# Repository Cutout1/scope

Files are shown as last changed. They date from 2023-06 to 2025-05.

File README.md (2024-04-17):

# Scopocket: A Low-Cost Oscilloscope for Education
Welcome to the GitHub repository for the Scopocket project. Here you can find the schematics, PCB fabrication files, and source code for the Scopocket. For additional information please visit [the documentation webpage.](https://scopocket.com)

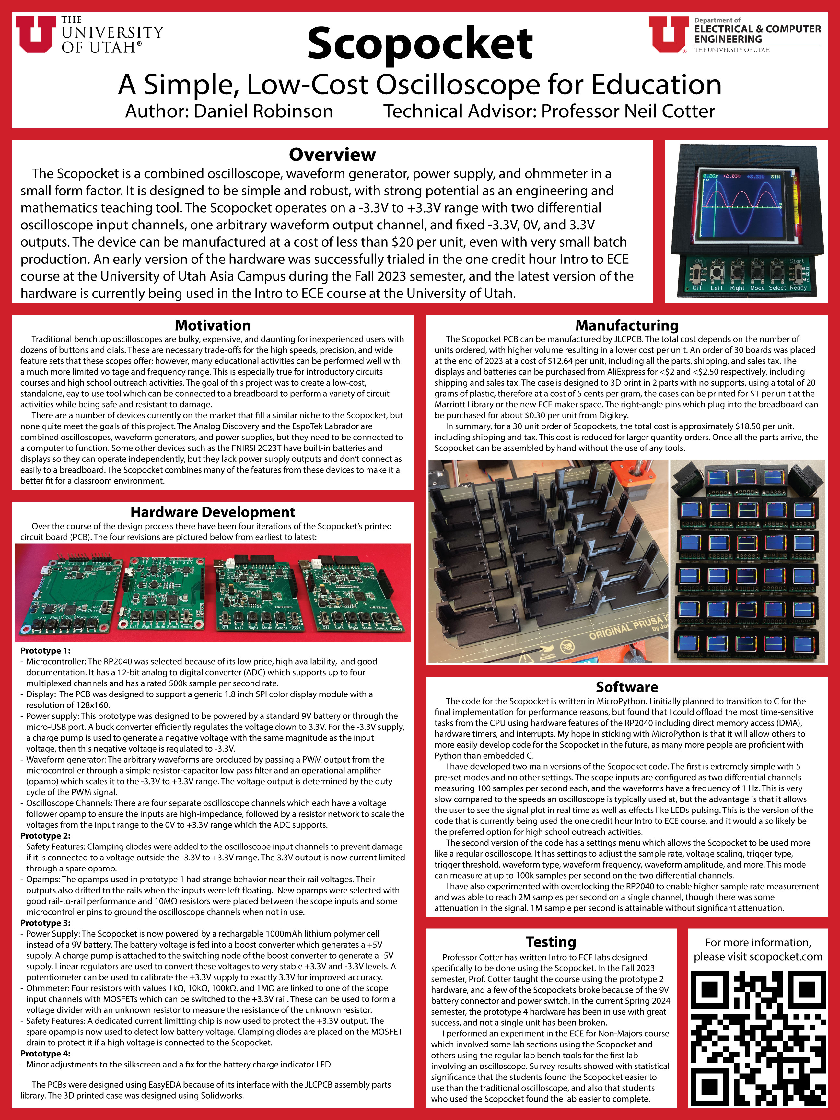
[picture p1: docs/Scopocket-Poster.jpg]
Scopocket Poster


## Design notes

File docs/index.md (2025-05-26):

---
layout: default
title: Scopocket
auto_title: false
---

# Overview

The Scopocket is a combined oscilloscope, function generator, ohmmeter, power supply, and more in a simple and compact package. It is primarily designed to be an educational tool with its main strengths being ease of use and low cost (being manufacturable for less than $20 per unit), with the tradeoff of having a quite limited voltage and frequency range.

The schematics, PCB fabrication files, source code, and case 3D models can all be found in [the GitHub repository.](https://github.com/Cutout1/scope)

A collection of lab activities designed to teach math concepts using the Scopocket can be found [on this Canvas site.](https://utah.instructure.com/courses/1191496)

The navigation bar on the left contains links to a number of informational pages.

Scopocket

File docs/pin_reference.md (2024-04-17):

---
id: pin-reference
title: Pin Reference
---

This page gives a detailed breakdown of what each pin on the Scopocket does. There are also pin labels on the underside of the Scopocket.

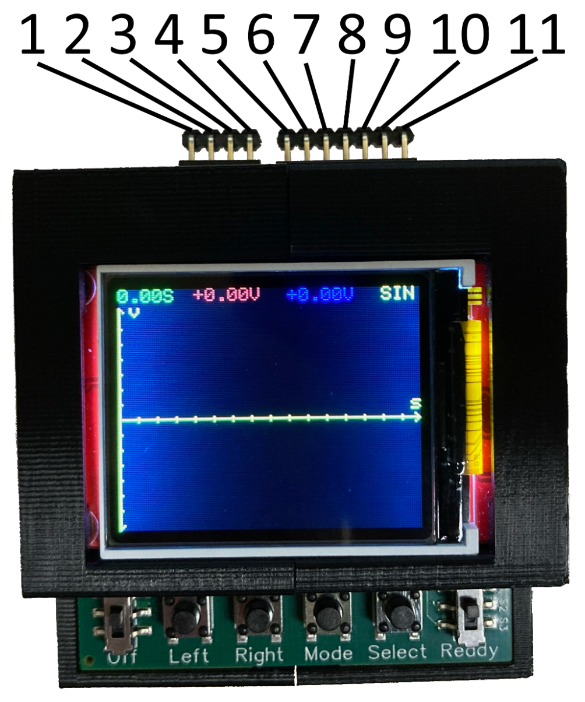
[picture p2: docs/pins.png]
Scopocket Pins


1. **Channel 1 Reference:** Reference voltage input for the oscilloscope’s first channel, which is plotted in red.
2. **Channel 1:** Voltage input for the oscilloscope’s first channel. The value that is plotted is equal to the voltage at this pin subtracted by the voltage at pin 1.
3. **Channel 2 Reference:** Reference voltage input for the oscilloscope’s first channel, which is plotted in blue.
4. **Channel 2:** Voltage input for the oscilloscope’s first channel. The value that is plotted is equal to the voltage at this pin subtracted by the voltage at pin 3.
5. **3.3V Output:** This pin outputs a steady 3.3V, limited to 75mA.
6. **0V Reference:** This pin outputs 0V.
7. **-3.3V Output:** This pin outputs a steady negative 3.3V, limited to 250mA.
8. **Switch 1:** This pin is connected to pin 9 when the switch is in the “Start” position.
9. **Switch 2:** This pin is connected to pin 8 when the switch is in the “Start” position, and it is connected to pin 10 when the switch is in the “Ready” position.
10. **Switch 3:** This pin is connected to pin 9 when the switch is in the “Ready” position.
11. **Waveform Output:** A configurable waveform is output with an amplitude up to 3.3V.

## Buttons and Switches
**Power Switch:** The switch on the left turns the Scopocket on and off. To preserve battery life, turn the Scopocket off when not in use.

**Left Button:** The left button is used to move the cursor left when reading a measured waveform. It may also be used to navigate the settings menu.

**Right Button:** The right button is used to move the cursor right when reading a measured waveform. It may also be used to navigate the settings menu.

**Mode Button:** The mode button is used to change the current settings of the Scopocket.

**Select Button:** The select button is used in the settings menu to select the currently underlined option. (Advanced software only)

**Trigger switch:** A recording can be triggered by moving the switch on the right from the “Ready” position to the “Start” position. It also changes the connection between pins 8, 9 and 10, as described in the previous section.

## Modes (Simple software only)
**SIN:** 2-channel oscilloscope sampling at 100 samples per second with a 1 Hz sine wave output from the waveform generator. Measurement begins immediately when the trigger switch is moved from “Ready” to “Start.”

**SQR:** 2-channel oscilloscope sampling at 100 samples per second with a 1 Hz square wave output from the waveform generator. Measurement begins immediately when the trigger switch is moved from “Ready” to “Start.”

**PHS:** 2-channel oscilloscope sampling at 100 samples per second with a 1 Hz sine wave output from the waveform generator. Measurement begins at the next peak of the output sine wave after the trigger switch is moved from “Ready” to “Start.”

**PWR:** This mode plots the power draw of a component in series with a 1kΩ resistor. To perform the measurement, place the channel 1 probes across a 1kΩ resistor in series with the load, and place the channel 2 probes across the load. Measurement begins when the load current reaches a peak. The power measurement is sampled at 100 samples per second, and a 1 Hz sine wave is output from the waveform generator.

**OHM:** Resistance measurement mode. To perform measurement, connect a resistor or resistor network between the channel 1 input and ground (pin 2 and pin 6). The screen will immediately display the resistance value in ohms.

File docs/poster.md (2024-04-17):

---
id: poster
title: Poster
auto_title: false
---

Scopocket Poster

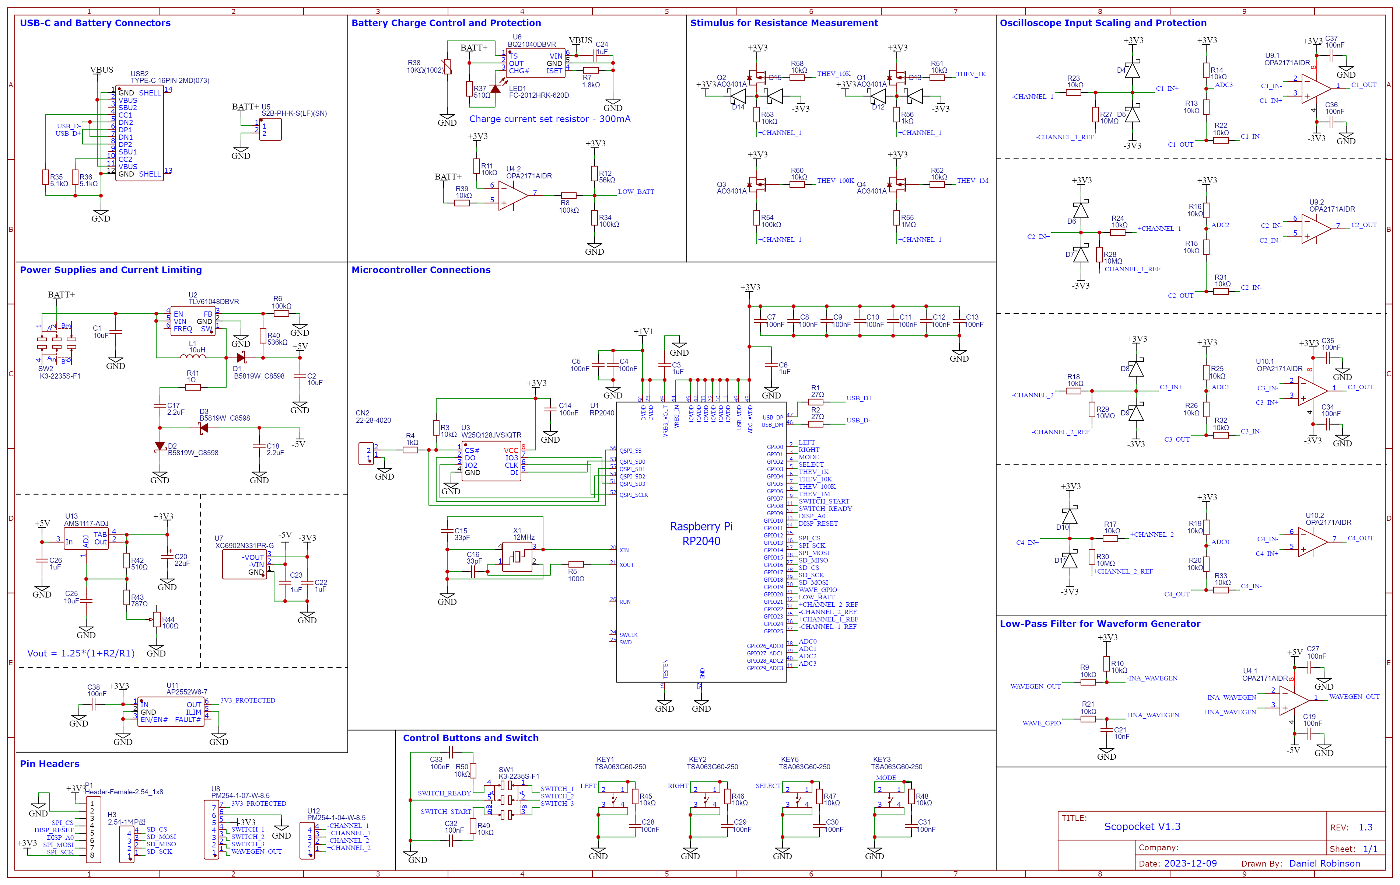
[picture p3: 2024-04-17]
Schematic/Scopocket Schematic V1.3.png

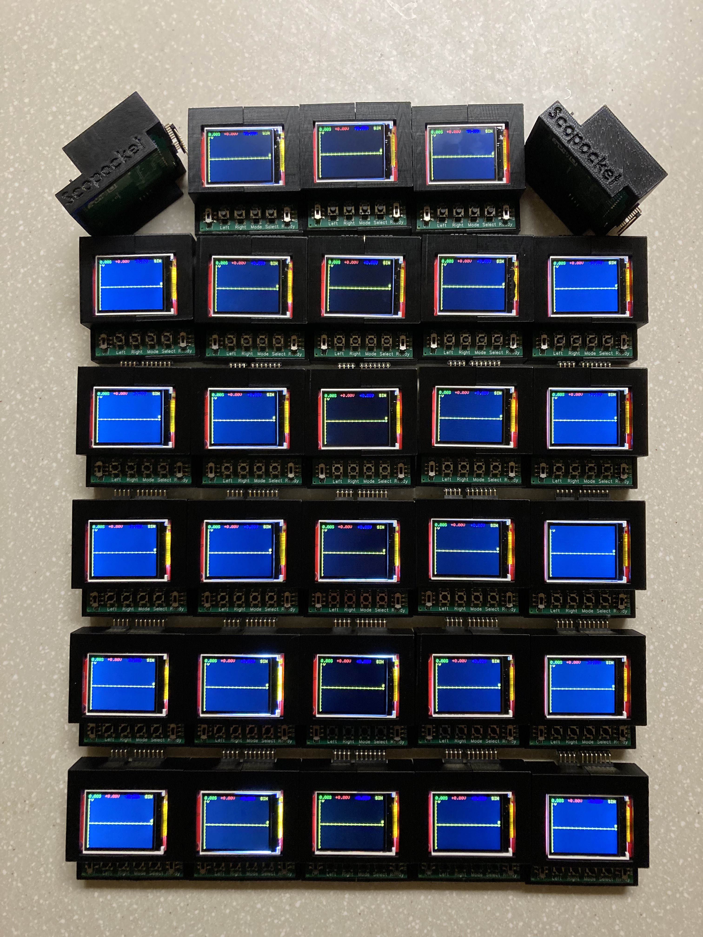
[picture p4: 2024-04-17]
docs/Thirty-Scopockets.jpg

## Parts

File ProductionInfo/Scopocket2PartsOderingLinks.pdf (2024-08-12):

Scopocket 2 Parts Ordering Links as of 2024/06/27

Batteries:
Ali Express
https://www.aliexpress.us/item/2251832658151463.html
10 PCS 3.7V 1000mAh 503450 Lithium Polymer LiPo Rechargeable Battery JST PH 2.0 2pin Plug For Mp3 DVD PAD Camera Recorder

Displays (Be sure to select the 1.8 TFT option) :
Ali Express
https://www.aliexpress.us/item/2255801096152347.html
TFT Display 0.96/1.3/1.44/1.77/1.8/2.0/2.4/2.8 inch IPS 7P SPI HD 65K Full Color LCD Module ST7735 Drive IC 80*160 For Arduino

Headers (40-pin headers may be manually snapped apart to make 3 7-pin headers, 4 4-pin headers) Digi-Key part number: S1132EC-40-ND (https://www.digikey.com/en/products/detail/sullins-connector-solutions/PRPC040SBCN-M71RC/2776146?s=N4IgTCBcDaIMoEYEGYwFEDCBaALABiwDkAREAXQF8g)
Manufacturer part number: PRPC040SB CN-M71RC (Sullins Connector Solutions)
Part Description: Conn Header R/A 40pos 2.54mm
100 @ $0.8275 = $82.75

Fish paper (battery insulator)
145ptags.com
https://www.145ptags.com/product-page/cg100325ftd-fish-paper-roll-3in-x-25ft-dark 145ptags.com
CG100325FTD Fish Paper Roll 3in. x 25' x 0.01" (Dark)

OBS:
Fish paper (battery insulator)
Digi-Key part number 36-117-ND (https://www.digikey.com/en/products/detail/keystone-electronics/117/7385294)
Manufacturer: Keystone Electronics Battery Insulator Pull Tab 1=1PC 500 @ $0.06554 = $32.77

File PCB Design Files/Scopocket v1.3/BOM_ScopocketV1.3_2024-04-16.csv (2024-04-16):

ID | Name | Designator | Footprint | Quantity | Manufacturer Part | Manufacturer | Supplier | Supplier Part | Price | Pins
1 | 100nF | C4,C5,C7,C8,C9,C10,C11,C12,C13,C14,C19,C27,C28,C29,C30,C31,C32,C33,C34,C35,C36,C37,C38 | C0402 | 23 | CL05B104KO5NNNC | SAMSUNG(三星) | LCSC | C1525 | 0.001 | 2
2 | 10KΩ(1002) | R38 | R0603 | 1 | NCP18XH103F03RB | muRata(村田) | LCSC | C13564 | 0.032 | 2
3 | Header-Female-2.54_1x8 | P1 | HDR-TH_8P-P2.54-V-F-1 | 1 | 2.54-1*8P母环保 | BOOMELE(博穆精密) | LCSC | C27438 | 0.07 | 8
4 | K3-2235S-F1 | SW1,SW2 | SW-SMD_K3-2235S-F1 | 2 | K3-2235S-F1 | 韩国韩荣 | LCSC | C223858 | 0.139 | 6
5 | OPA2171AIDR | U9,U4,U10 | SOIC-8_L5.0-W4.0-P1.27-LS6.0-BL | 3 | OPA2171AIDR | TI(德州仪器) | LCSC | C40904 | 0.356 | 8
6 | PM254-1-07-W-8.5 | U8 | HDR-TH_7P-P2.54-H-F-W10.0-N | 1 | PM254-1-07-W-8.5 | HCTL(华灿天禄) | LCSC | C2897389 | 0.147 | 7
7 | PM254-1-04-W-8.5 | U12 | HDR-TH_4P-P2.54-H-F-W10.0-N | 1 | PM254-1-04-W-8.5 | HCTL(华灿天禄) | LCSC | C2897386 | 0.096 | 4
8 | 10uF | C1,C2 | C0603 | 2 | CL10A106MA8NRNC | SAMSUNG(三星) | LCSC | v |  | 2
9 | 10uF | C25 | C0603 | 1 | CL10A106MA8NRNC | SAMSUNG(三星) | LCSC | C96446 | 0.017 | 2
10 | 1uF | C3,C6,C22,C23,C26,C24 | C0402 | 6 | CL05A105KA5NQNC | SAMSUNG | LCSC | C52923 | 0.004 | 2
11 | 33pF | C15,C16 | C0402 | 2 | 0402CG330J500NT | FH | LCSC | C1562 | 0.001 | 2
12 | 10nF | C21 | C0402 | 1 | CL05B103KB5NNNC | SAMSUNG(三星) | LCSC | C15195 | 0.001 | 2
13 | 2.2uF | C17,C18 | C1206 | 2 | CL31B225KBHNNNE | SAMSUNG(三星) | LCSC | C50254 | 0.028 | 2
14 | 22uF | C20 | CASE-A_3216 | 1 | CA45-A-10V-22uF-K | CEC(振华新云) | LCSC | C129272 | 0.064 | 2
15 | B5819W_C8598 | D1,D2,D3 | SOD-123_L2.7-W1.6-LS3.7-RD-1 | 3 | B5819W SL | CJ(江苏长电/长晶) | LCSC | C8598 | 0.025 | 2
16 | BAS100CS-AU_R1_000A1 | D4,D5,D6,D7,D8,D9,D10,D11,D12,D13,D14,D15 | SOD-323 | 12 | BAS100CS-AU_R1_000A1 | PANJIT International | LCSC | C2999088 | 0.056 | 2
17 | 2.54-1*4P母 | H3 | HDR-TH_4P-P2.54-V-F | 1 | 2.54-1*4P母 | BOOMELE(博穆精密) | LCSC | C2718488 | 0.041 | 4
18 | TSA063G60-250 | KEY1,KEY2,KEY3,KEY5 | KEY-SMD_4P-L6.1-W6.1-P4.50-LS9.0 | 4 | TSA063G60-250 | BRIGHT(博瑞泰) | LCSC | C294566 | 0.025 | 4
19 | 10uH | L1 | IND-SMD_L4.0-W4.0 | 1 | SWPA4030S100MT | Sunlord(顺络) | LCSC | C38117 | 0.046 | 2
20 | FC-2012HRK-620D | LED1 | LED0805-R-RD | 1 | NCD0805R1 | 国星光电 | LCSC | C84256 | 0.012 | 2
21 | AO3401A | Q1,Q2,Q3,Q4 | SOT-23_L2.9-W1.3-P1.90-LS2.4-BR | 4 | AO3401A | AOS | LCSC | C15127 | 0.053 | 3
22 | 27Ω | R1,R2 | R0603 | 2 | 0603WAF270JT5E | UniOhm | LCSC | C25190 | 0.001 | 2
23 | 10kΩ | R3,R9,R10,R11,R13,R14,R15,R16,R17,R18,R19,R20,R21,R22,R23,R24,R25,R26,R31,R32,R33,R39,R45,R46,R47,R48,R49,R50,R51,R53,R58,R60,R62 | R0603 | 33 | 0603WAF1002T5E | UniOhm | LCSC | C25804 | 0.001 | 2
24 | 1kΩ | R4,R56 | R0603 | 2 | 0603WAF1001T5E | UniOhm | LCSC | C21190 | 0.001 | 2
25 | 100kΩ | R6,R8,R34,R54 | R0603 | 4 | 0603WAF1003T5E | UNI-ROYAL(厚声) | LCSC | C25803 | 0.001 | 2
26 | 100Ω | R5 | R0402 | 1 | 0402WGF1000TCE | UniOhm | LCSC | C25076 | 0.001 | 2
27 | 1.8kΩ | R7 | R0603 | 1 | 0603WAF1801T5E | UNI-ROYAL(厚声) | LCSC | C4177 | 0.001 | 2
28 | 56kΩ | R12 | R0603 | 1 | 0603WAF5602T5E | UNI-ROYAL(厚声) | LCSC | C23206 | 0.001 | 2
29 | 510Ω | R37,R42 | R0603 | 2 | 0603WAF5100T5E | UNI-ROYAL(厚声) | LCSC | C23193 | 0.001 | 2
30 | 536kΩ | R40 | R0603 | 1 | RS-03K5363FT | FH(风华) | LCSC | C321940 | 0.001 | 2
31 | 787Ω | R43 | R0603 | 1 | 0603WAF7870T5E | UNI-ROYAL(厚声) | LCSC | C23111 | 0.001 | 2
32 | 1MΩ | R55 | R0603 | 1 | 0603WAF1004T5E | UNI-ROYAL(厚声) | LCSC | C22935 | 0.001 | 2
33 | 10MΩ | R27,R28,R29,R30 | R0402 | 4 | RTT02106JTH | RALEC(旺诠) | LCSC | C102764 |  | 2
34 | 5.1kΩ | R35,R36 | R0402 | 2 | RC-02W5101FT | FH(风华) | LCSC | C294638 | 0.001 | 2
35 | 1Ω | R41 | R1206 | 1 | 1206W4F100KT5E | UNI-ROYAL(厚声) | LCSC | C17928 | 0.004 | 2
36 | 100Ω | R44 | RES-ADJ-SMD_VG039NCH | 1 | VG039NCHXTB101 | HDK(北陆电气) | LCSC | C128542 | 0.067 | 3
37 | RP2040 | U1 | LQFN-56_L7.0-W7.0-P0.4-EP | 1 | RP2040 | Raspberry Pi(树莓派) | LCSC | C2040 | 0.988 | 57
38 | TLV61048DBVR | U2 | SOT-23-6_L2.9-W1.6-P0.95-LS2.8-BR | 1 | TLV61048DBVR | TI(德州仪器) | LCSC | C2861467 | 0.216 | 6
39 | BQ21040DBVR | U6 | SOT-23-6_L2.9-W1.6-P0.95-LS2.8-BR | 1 | BQ21040DBVR | TI(德州仪器) | LCSC | C202311 | 0.24 | 6
40 | W25Q128JVSIQTR | U3 | SOIC-8_L5.3-W5.3-P1.27-LS8.0-BL | 1 | W25Q128JVSIQTR | WINBOND | LCSC | C97521 | 0.583 | 8
41 | XC6902N331PR-G | U7 | SOT-89-3_L4.5-W2.5-P1.50-LS4.2-BR | 1 | XC6902N331PR-G | TOREX(特瑞仕) | LCSC | C165899 | 0.596 | 3
42 | AP2552W6-7 | U11 | SOT-26_L3.0-W1.6-P0.95-LS2.8-BL | 1 | AP2552W6-7 | DIODES(美台) | LCSC | C441824 | 0.196 | 6
43 | AMS1117-ADJ | U13 | SOT-223_L6.7-W3.5-P2.30-BR | 1 | AMS1117-ADJ | AMS | LCSC | C6188 | 0.103 | 4
44 | TYPE-C 16PIN 2MD(073) | USB2 | USB-C-SMD_TYPE-C-6PIN-2MD-073 | 1 | TYPE-C 16PIN 2MD(073) | SHOU HAN(首韩) | LCSC | C2765186 | 0.05 | 16
45 | 12MHz | X1 | OSC-SMD_4P-L3.2-W2.5-BL | 1 | X322512MSB4SI | YXC | LCSC | C9002 | 0.058 | 4
46 | S2B-PH-K-S(LF)(SN) | U5 | CONN-TH_S2B-PH-K-S-LF-SN | 1 | S2B-PH-K-S(LF)(SN) | JST | LCSC | C173752 | 0.026 | 2

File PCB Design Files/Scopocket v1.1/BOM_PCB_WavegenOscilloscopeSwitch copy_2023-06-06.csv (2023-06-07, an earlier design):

ID | Name | Designator | Footprint | Quantity | Manufacturer Part | Manufacturer | Supplier | Supplier Part | Price
1 | 1uF | C22,C23,C3,C6 | C0402 | 4 | CL05A105KA5NQNC | SAMSUNG | LCSC | C52923 | 0.004
2 | XC6902N331PR-G | U7 | SOT-89-3_L4.5-W2.5-P1.50-LS4.2-BR | 1 | XC6902N331PR-G | TOREX(特瑞仕) | LCSC | C165899 | 0.662
3 | 10kΩ | R22,R31,R32,R33,R17,R18,R19,R20,R23,R24,R25,R26,R3,R9,R10,R11,R12,R13,R14,R15,R16,R21 | R0603 | 22 | 0603WAF1002T5E | UniOhm | LCSC | C25804 | 0.001
4 | 22-28-4020 | CN3,CN1 | HDR-TH_2P-P2.54-V-M-1 | 2 | 22284020 | MOLEX | LCSC | C234182 | 0.062
5 | OPA2171AIDR | U4,U9,U10 | SOIC-8_L5.0-W4.0-P1.27-LS6.0-BL | 3 | OPA2171AIDR | TI(德州仪器) | LCSC | C40904 | 0.823
6 | Z-211-0411-0021-001 | H4,H1 | HDR-TH_4P-P2.54-V-M | 2 | Z-21104110021001 | Nextron(正凌) | LCSC | C152150 | 0.029
7 | 10MΩ | R27,R28,R29,R30 | R0402 | 4 | RTT02106JTH | RALEC(旺诠) | LCSC | C102764
8 | BAS100CS-AU_R1_000A1 | D4,D5,D6,D7,D8,D9,D10,D11 | SOD-323 | 8 | BAS100CS-AU_R1_000A1 | PANJIT International | LCSC | C2999088 | 0.054
9 | PZ254V-11-07P | H2 | HDR-TH_7P-P2.54-V-M | 1 | PZ254V-11-07P | XFCN(兴飞) | LCSC | C492406 | 0.034
10 | 2.54-1*4P母 | H3 | HDR-TH_4P-P2.54-V-F | 1 | 2.54-1*4P母 | BOOMELE(博穆精密) | LCSC | C2718488 | 0.042
11 | 2685Y-108CNG1SNA01 | U19 | HDR-TH_8P-P2.54-V-F-1 | 1 | 2685Y-108CNG1SNA01 | 华宇创 | LCSC | C350308 | 0.079
12 | JS202011SCQN | SW1 | SW-SMD_JS202011SCQN | 1 | JS202011SCQN | C&K | LCSC | C221666 | 0.52
13 | TSA063G60-250 | KEY5,KEY1,KEY2,KEY3 | KEY-SMD_4P-L6.1-W6.1-P4.50-LS9.0 | 4 | TSA063G60-250 | BRIGHT(博瑞泰) | LCSC | C294566 | 0.029
14 | 10uF | C1,C17,C18 | C0603 | 3 | CL10A106MA8NRNC | SAMSUNG(三星) | LCSC | v
15 | 22uF | C2 | C0603 | 1 | CL10A226MQ8NRNC | SAMSUNG(三星) | LCSC | C59461 | 0.01
16 | 33pF | C15,C16 | C0402 | 2 | 0402CG330J500NT | FH | LCSC | C1562 | 0.001
17 | 10nF | C21 | C0402 | 1 | CL05B103KB5NNNC | SAMSUNG(三星) | LCSC | C15195 | 0.001
18 | 100nF | C4,C5,C7,C8,C9,C10,C11,C12,C13,C14 | C0402_NEW | 10 | CL05B104KO5NNNC | SAMSUNG | LCSC | C1525 | 0.001
19 | B5819W_C8598 | D1,D2,D3 | SOD-123_L2.7-W1.6-LS3.7-RD-1 | 3 | B5819W SL | CJ(江苏长电/长晶) | LCSC | C8598 | 0.03
20 | 2.2uH | L1 | IND-SMD_L3.0-W3.0 | 1 | CKCS3015-2.2uH/M | CENKER(岑科) | LCSC | C354563 | 0.049
21 | 27Ω | R1,R2 | R0603 | 2 | 0603WAF270JT5E | UniOhm | LCSC | C25190 | 0.001
22 | 1kΩ | R4 | R0603 | 1 | 0603WAF1001T5E | UniOhm | LCSC | C21190 | 0.001
23 | 100kΩ | R6 | R0603 | 1 | 0603WAF1003T5E | UNI-ROYAL(厚声) | LCSC | C25803 | 0.001
24 | 100Ω | R5 | R0402 | 1 | 0402WGF1000TCE | UniOhm | LCSC | C25076 | 0.001
25 | MK-12C02-G020 | SW2 | SW-SMD_MK-12C02-G020 | 1 | MK-12C02-G020 | G-Switch | LCSC | C963206 | 0.058
26 | RP2040 | U1 | LQFN-56_L7.0-W7.0-P0.4-EP | 1 | RP2040 | Raspberry Pi(树莓派) | LCSC | C2040 | 1.066
27 | TPS62172DSGR | U2 | WSON-8_L2.0-W2.0-P0.50-TL-EP | 1 | TPS62172DSGR | TI(德州仪器) | LCSC | C59873 | 0.953
28 | W25Q128JVSIQTR | U3 | SOIC-8_L5.3-W5.3-P1.27-LS8.0-BL | 1 | W25Q128JVSIQTR | WINBOND | LCSC | C97521 | 0.656
29 | ICL7660AIBAZA-T | U5 | SOIC-8_L5.0-W4.0-P1.27-LS6.0-BL | 1 | ICL7660AIBAZA-T | RENESAS(瑞萨)/IDT | LCSC | C7881 | 0.649
30 | MICROXNJ | USB1 | MICRO-USB-SMD_MICROXNJ | 1 | MicroXNJ | SHOU HAN | LCSC | C404969 | 0.034
31 | 12MHz | X1 | OSC-SMD_4P-L3.2-W2.5-BL | 1 | X322512MSB4SI | YXC | LCSC | C9002 | 0.068

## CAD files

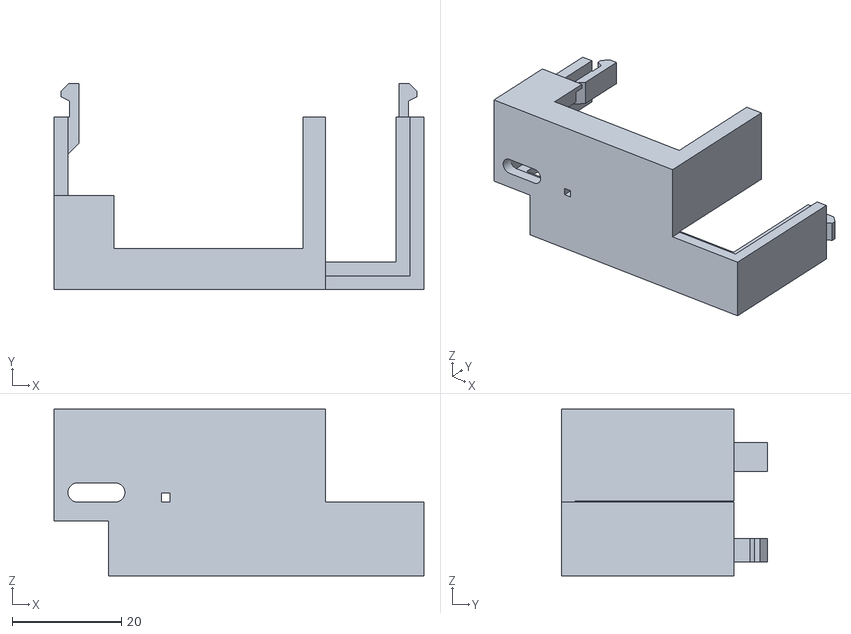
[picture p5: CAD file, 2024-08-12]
Case Design Files/Case With Pin Label Slot/scopocket_case_left.STL
67.6 x 37.7 x 30.5

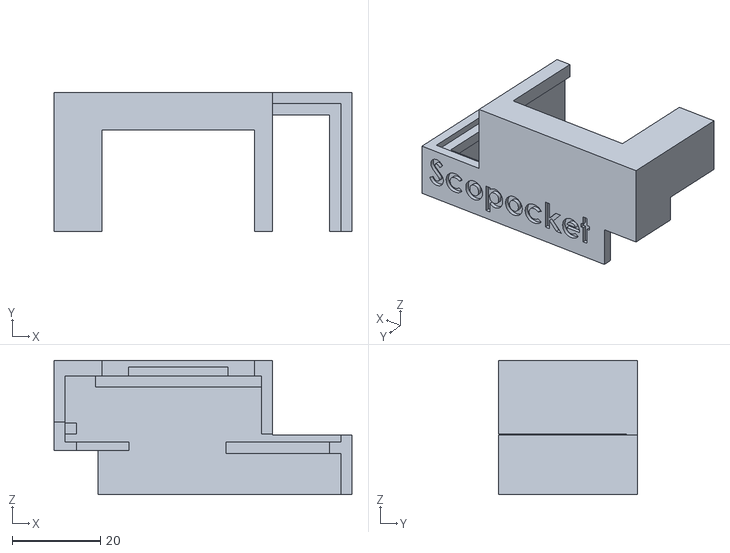
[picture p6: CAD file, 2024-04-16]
Case Design Files/Case Without Pin Labels/scopocket_case_right.STL
67.6 x 31.5 x 30.5

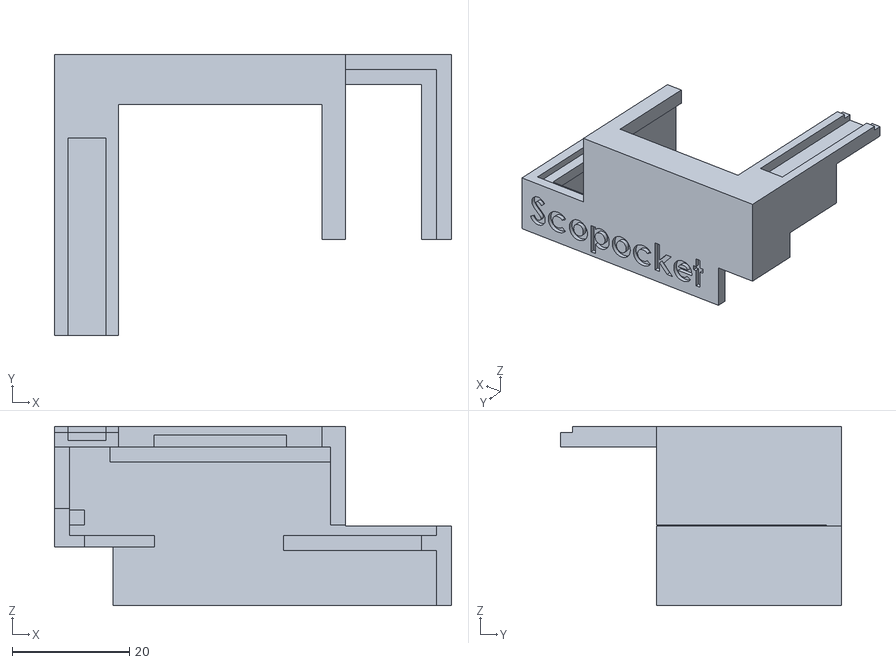
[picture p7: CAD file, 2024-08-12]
Case Design Files/Case With Pin Label Slot/scopocket_case_right.STL
67.6 x 47.8 x 30.5

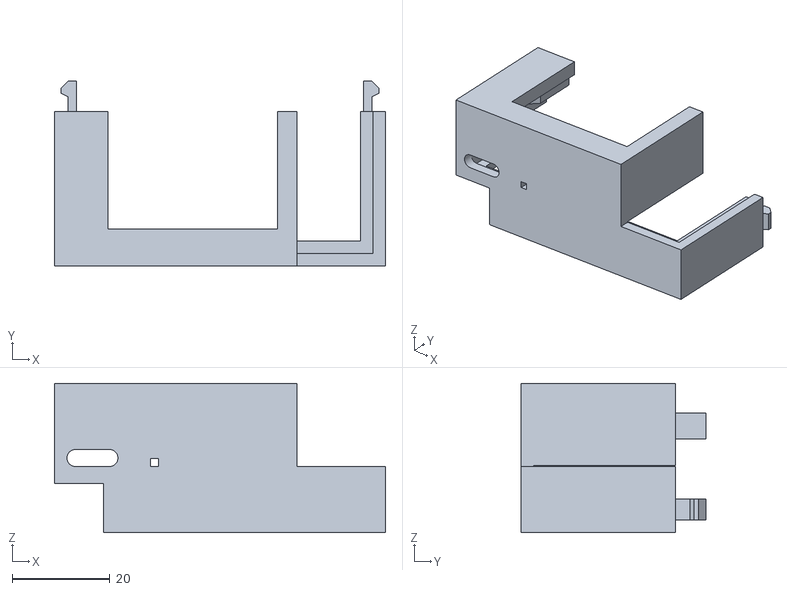
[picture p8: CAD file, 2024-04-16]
Case Design Files/Case Without Pin Labels/scopocket_case_left.STL
67.6 x 37.7 x 30.5

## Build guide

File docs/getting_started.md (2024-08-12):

---
id: getting-started
title: Getting Started
---

This page assumes you have a fully assembled and programmed Scopocket. If you do not, please visit [the manufacturing page](https://scopocket.com/manufacturing.html) for information on how to construct one.

For a description of what each pin on the Scopocket does, visit the [pin reference page.](https://scopocket.com/pin_reference.html) The pin reference page also describes the usage of each button and what each mode in the "simple" software version does.

In the future, this page will have a full written explanation with images explaining how to use the Scopocket in depth. For now, please review [this video](https://www.youtube.com/watch?v=SbrOokjkZqg) for a demonstration and explanation.

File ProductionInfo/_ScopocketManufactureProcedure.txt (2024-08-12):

_ScopocketManufactureProcedure.txt

Buying missing parts for PCB
necotter dropdown: Manage Parts
JLCPCB Parts

Buying Scopoket Boards

Login to JLCPCB

Go to Order Now link (next to users icon upper right)

New tab.  Go to Scopocket.com
Click Getting Started
Click on manufacturing page
Under Printed Circuit Board
  Click "here in the GitHub repository"
Click on each file and then click on download icon after file comes up
It is okay that files show up as gibberish before download
  No need to unzip the Gerber file
Back to JLCPCB site
click Upload Gerber file link (upload from mac downloads folder)

* = non-default value

Default on top row should be "Standard PCB/PCBA"
Base Material: FR-4
Layers: 4
Dimensions: 57.33 * 62 (should self-populate)
*PCB QTY 30

Industrial/Consumer electronics

--PCB Specifications--
Different Design: 1
 *Delivery Format: Panel by JLCPCB
 *Panel Format: Column: 2 (57.33mm) Row: 2 (62mm)  [4 bds per panel]
 *Edge Rails: On 2 sides
 *Panel size: X: (57.33 x 2 + 5*2 (Edge Rails) ) = 124.660 mm Y : ( 62 x 2 ) = 124.000 mm
PCB Thickness: 1.6
PCB Color: Green
Silkscreen: White
Material Type: FR4-Standard TG 135-140
*Surface Finish: LeadFree HASL

--High-Spec Options--
Outer Copper Weight: 1 oz
Inner Copper Weight: 0.5 oz
Specify Layer Sequence: No
*Impedance Control: Yes  use JLC04161H-7628
Via Covering: Plugged
Min via hole size/diameter: 0.3mm/(0.4/0.45mm)
Board Outline Tolerance: ±0.2mm(Regular)
*Confirm Production file:  (check email to confirm production)
*Remove Order Number: Specify a location (the location is already written on bd)
Flying Probe Test: Fully Test
Gold Fingers: No
Castellated Holes: No
Edge Plating: No

--Advanced Options--   Note dropdown menu, but no changes needed.
4-Wire Kelvin Test: No
Paper between PCBs: No
Appearance Quality: IPC Class 2 Standard
Silkscreen Technology: Ink-jet/Screen Printing Silkscreen
X-out board: Accept
Package Box With JLCPCB logo
PCB Remark: 

Click PCB Assembly switch
PCBA Type: Standard
Assembly Side: Top Side
PCBA Qty: 30  (there will be 4 Scopockets on each PCB)
Edge Rails/Fiducials: Added by JLCPCB
*Confirm Parts Placement: Yes  (look for email)

Advanced Options
Photo Confirmation: No             Board Cleaning: No
Conformal Coating: No              Bake Components: No
Packaging: Antistatic bubble film  *Depanel boards & edge rail before delivery: Yes
Solder Paste: Sn96.5%, Ag3.0%,Cu0.5%(260°)  Add paste for unpopulated pad & step stencil opening: No
Others: No

Click CONFIRM

NEXT
Upload BOM and PickAndPlace files
Click: Process BOM & CPL
Check parts list to see if any parts missing (can be ordered thru JLCPCB)
Check that all parts are in place
NEXT
Pop up Confirm Production file and Parts Placement: Confirm

If part at bottom is in red, then it must be ordered.  Click on their part number and copy it (starts with C).  Click Next.  Do not place (the part).  Click Place Order (to order part).  Can "edit order" later from starting page.

Hover over username, click Parts Manager to order parts
Qnty add 10 or so extra
Click add to my parts lib for assmbly

If all parts are available for the order, Confirm.

Product Description:  Sensor\Controller\Precision Instrument/Research/Education/...  Multimeter
Save to CART
Boards and Assembly show up as separate costs
Secure Checkout
DHL Express Economy for shipping
Agree to Customer Compliance Statement
Submit Order

Check email for final design so can Confirm it and have boards made.
Usually takes a few hours for email to arrive.
Or on browser tab for PCB Prototype & PCB Fabrication, look for Reviewing to turn into "Review Production File"

To review production file:
Login to jlcpcb (same login as easyeda)
hover over login name and click order history

Note production of boards is done first.  After the boards are made, the placement of parts (soldering) production is done separately.

? Need instructions on the second production step

Older version of instructions after this
----------------------------------------

* PCB Assembly: click button to "on"
  Assemble top side (nothing is on bottom side)
PCBA Type: Standard (for small quantity can do Economic)
Assembly Side: Top Side
* PCBA Qty: 30  (panels, not boards)
Edge Rails/Fiducials: Added by JLCPCB

CONFIRM button
NEXT
Add BOM File (one of the files downloaded from Scopocket.com)
Add CPL File (The PickandPlace file downloaded from Scopocket.com)
Process BOM & CPL button
Look for shortfalls in last column at bottom (order elsewhere)
NEXT button
(Do not Place) if any shortfalls [write down the part numbers, they start with letter C so they can be ordered]
NEXT
Confirm parts placement, parts ?

Procedure for those with access to EasyEDA Project:
Goto easyeda.com
login: 

In future gerber files etc. will be uploaded to GitHub

Daniel R shared design with me on EasyEDA for now.

Note: to login to jlcpcb.com use same login info as for EasyEDA

Back to EasyEDA:
click on EasyEDA Designer
Editor Version: Std Edition

Click on ScopocketV1.3 on left side under Work Space: Personal : All Projects : Joined : ScopocketV1.3

Double Click on PCB_ScopocketV1.3
  brings up picture of PCB

Menu in top bar of EasyEDA page:
Click on Fabrication
Click on one-click order PCB/SMT
Yes, Check DRC  (design rule checking)

* Select Quantity: 120 (for example)
PCB Color: Green
Manufacturer: JLCPCB
Click on one-click order PCB/SMT  (lower right corner)
Click OK to continue after Gerber etc. generated finish
  if it gets stuck, close tab to go back one window
Build Time: as desired

Base Material: leave as is
Layers: leave as is
Dimensions: leave as is
Panel Qty: 30  (panels, not boards here)
Product Type: Industrial/Consumer electronics
Different Design: leave as 1
* Delivery Format: Panel by JLCPCB
* Panel Format: Column: 2 (57.33mm), Row: 2 (62mm)   4 bds per panel
* Edge Rails: On 2 sides
Panel Size = just what they say it is

PCB Thinkness: leave as is
PCB color: green is cheapest
Silkscreen: white (only option!)
Material Type: FR4-Standard TG 135-140
* Surface Finish: LeadFree HASL  (environmentally better)
Outer Copper Weight: 1 oz.  (for higher current, use 2 oz)
Inner Copper Weight: 0.5 oz
Specify Layer Sequence: No  (o.w. submit separate files for layers?)
* Impedance Control: Yes  use JLC04161H-7628
Via Covering: Plugged
Min via hole size/diameter: 0.3mm/(0.40/0.45mm)
Board Outline Tolerance: ±0.2mm(Regular)
* Confirm Production file: Yes  (check email to confirm production)
* Remove Order Number: Specify a location (location already written on bd)
Flying Probe Test: Fully test
Gold Fingers: No
  (for gold edge connectors)
Castellated Holes: No
Edge Plating: No  (helps to have band of metal around edge for EMI)

Advanced Options:  Note dropdown menu, but no changes needed.
PCB Remark: none
* PCB Assembly: click button to "on"
  Assemble top side (nothing is on bottom side)
PCBA Type: Standard (for small quantity can do Economic)
Assembly Side: Top Side
* PCBA Qty: 30  (panels, not boards)
Edge Rails/Fiducials: Added by JLCPCB
* Confirm Parts Placement: Yes

Advanced Options:  Note dropdown menu
Photo Confirmation: No
Conformal Coating: No
Packaging: Antistatic bubble film
Solder Paster: Sn96.5%, Ag3.0%, Cu 0.5% (260°C)
Others: No
Board Cleaning: 
Bake Components:
Depanel boards & edge rail before delivery: Yes
Add paste for unpopulated pad & step stencil opening
Remark
I agree to Terms and Conditions of JLCPCB assembly Service 
click Confirm

Review appearance of board and click next
should show check marks next to Assembly-BOM and Assembly-CPL
File provided as: Single Piece, pls help me repeat the data
click Process BOM & CPL

Scroll through BOM and make sure all parts have select checked
If parts missing, call Daniel (also search icon on each part can be used to find replacement part)
click NEXT
Now board shows with BOM to right
NEXT
Confirm Parts Placement:  OK
Product Description: Sensor\Controller\Precision Instrument/Research/Education/...
Save to CART
Boards and Assembly show up as separate costs
Secure Checkout
DHL Express Economy for shipping
Agree to Customer Compliance Statement
Submit Order

Check email for final design so can Confirm it and have boards made.
Usually takes a few hours.
Or on browser tab for PCB Prototype & PCB Fabrication, look for Reviewing to turn into "Review Production File"

To review production file:
Login to jlcpcb (same login as easyeda)
hover over login name and click order history

*not default value

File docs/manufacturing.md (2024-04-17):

---
id: manufacturing
title: Manufacturing
---

There are four main components of the Scopocket: the printed circuit board (PCB), display, battery, and case. This page lists instructions for obtaining each of these components..

## Printed Circuit Board
The manufacturing files needed to fabricate and assemble a Scopocket PCB can be found [here in the GitHub repository.](https://github.com/Cutout1/scope/tree/main/PCB%20Design%20Files/Scopocket%20v1.3) This includes the gerber file outlining the design of the board itself, the bill of materials which lists all components that need to be placed on the board, and the pick-and-place file describing where the components should be placed on the PCB.

I recommend using JLCPCB to manufacture the PCB. More extensive documentation for ordering the PCB will be included here in the near future, but essentially you just need to go to [JLCPCB's order page](https://cart.jlcpcb.com/quote), upload the gerber file, select the quantity of boards you want to order, click the slider for PCB assembly, go to the next page and upload the BOM and pick-and-place files, verify that all the parts appear on the board view correctly, and place the order.

## Display
The display is a generic 1.8 inch TFT LCD display module with an SPI interface available from a number of sellers.

I have verified the module available [at this page](https://www.aliexpress.us/item/2255801096152347.html) as being compatible with the Scopocket, and it is currently available at a cost of $1.65 per unit. Be sure to select the "1.8 TFT" option.

## Battery
The Scopocket should be usable with any single-cell lithium ion or lithium polymer battery, though not all form-factors will fit well inside the case. The battery connector on the PCB is a 2.0mm JST connector.

I recommend [this battery](https://www.aliexpress.us/item/2251832658151463.html) which is currently being sold in quantities of 10 for $16.50, coincidentally resulting in a unit cost exactly the same as the display: $1.65.

## Case
The case for the Scopocket is designed to be 3D printed in two separate pieces that clip together around the device. The STL 3D model files can be found [here in the GitHub repository.](https://github.com/Cutout1/scope/tree/main/Case%20Design%20Files)

The case should be printable with its largest face on the print bed without supports, as pictured below. Lower quality 3D printers may need some support for the clip.

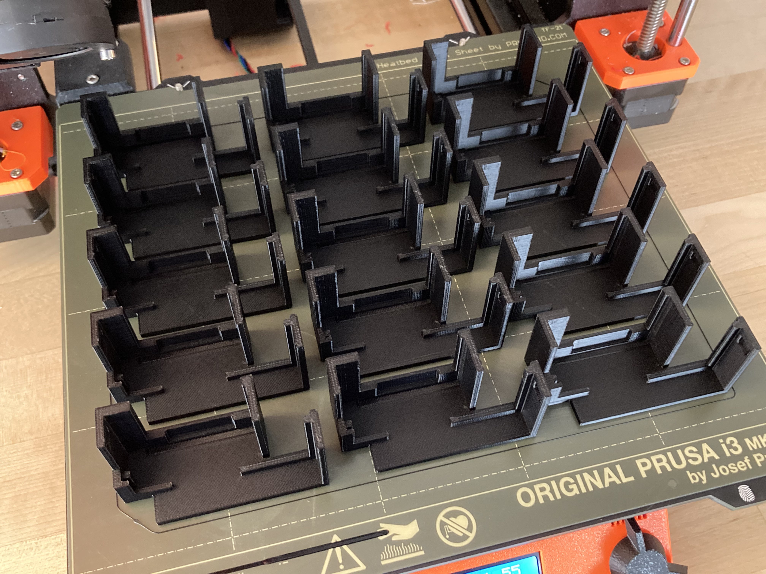
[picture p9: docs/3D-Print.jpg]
Scopocket Case Printing


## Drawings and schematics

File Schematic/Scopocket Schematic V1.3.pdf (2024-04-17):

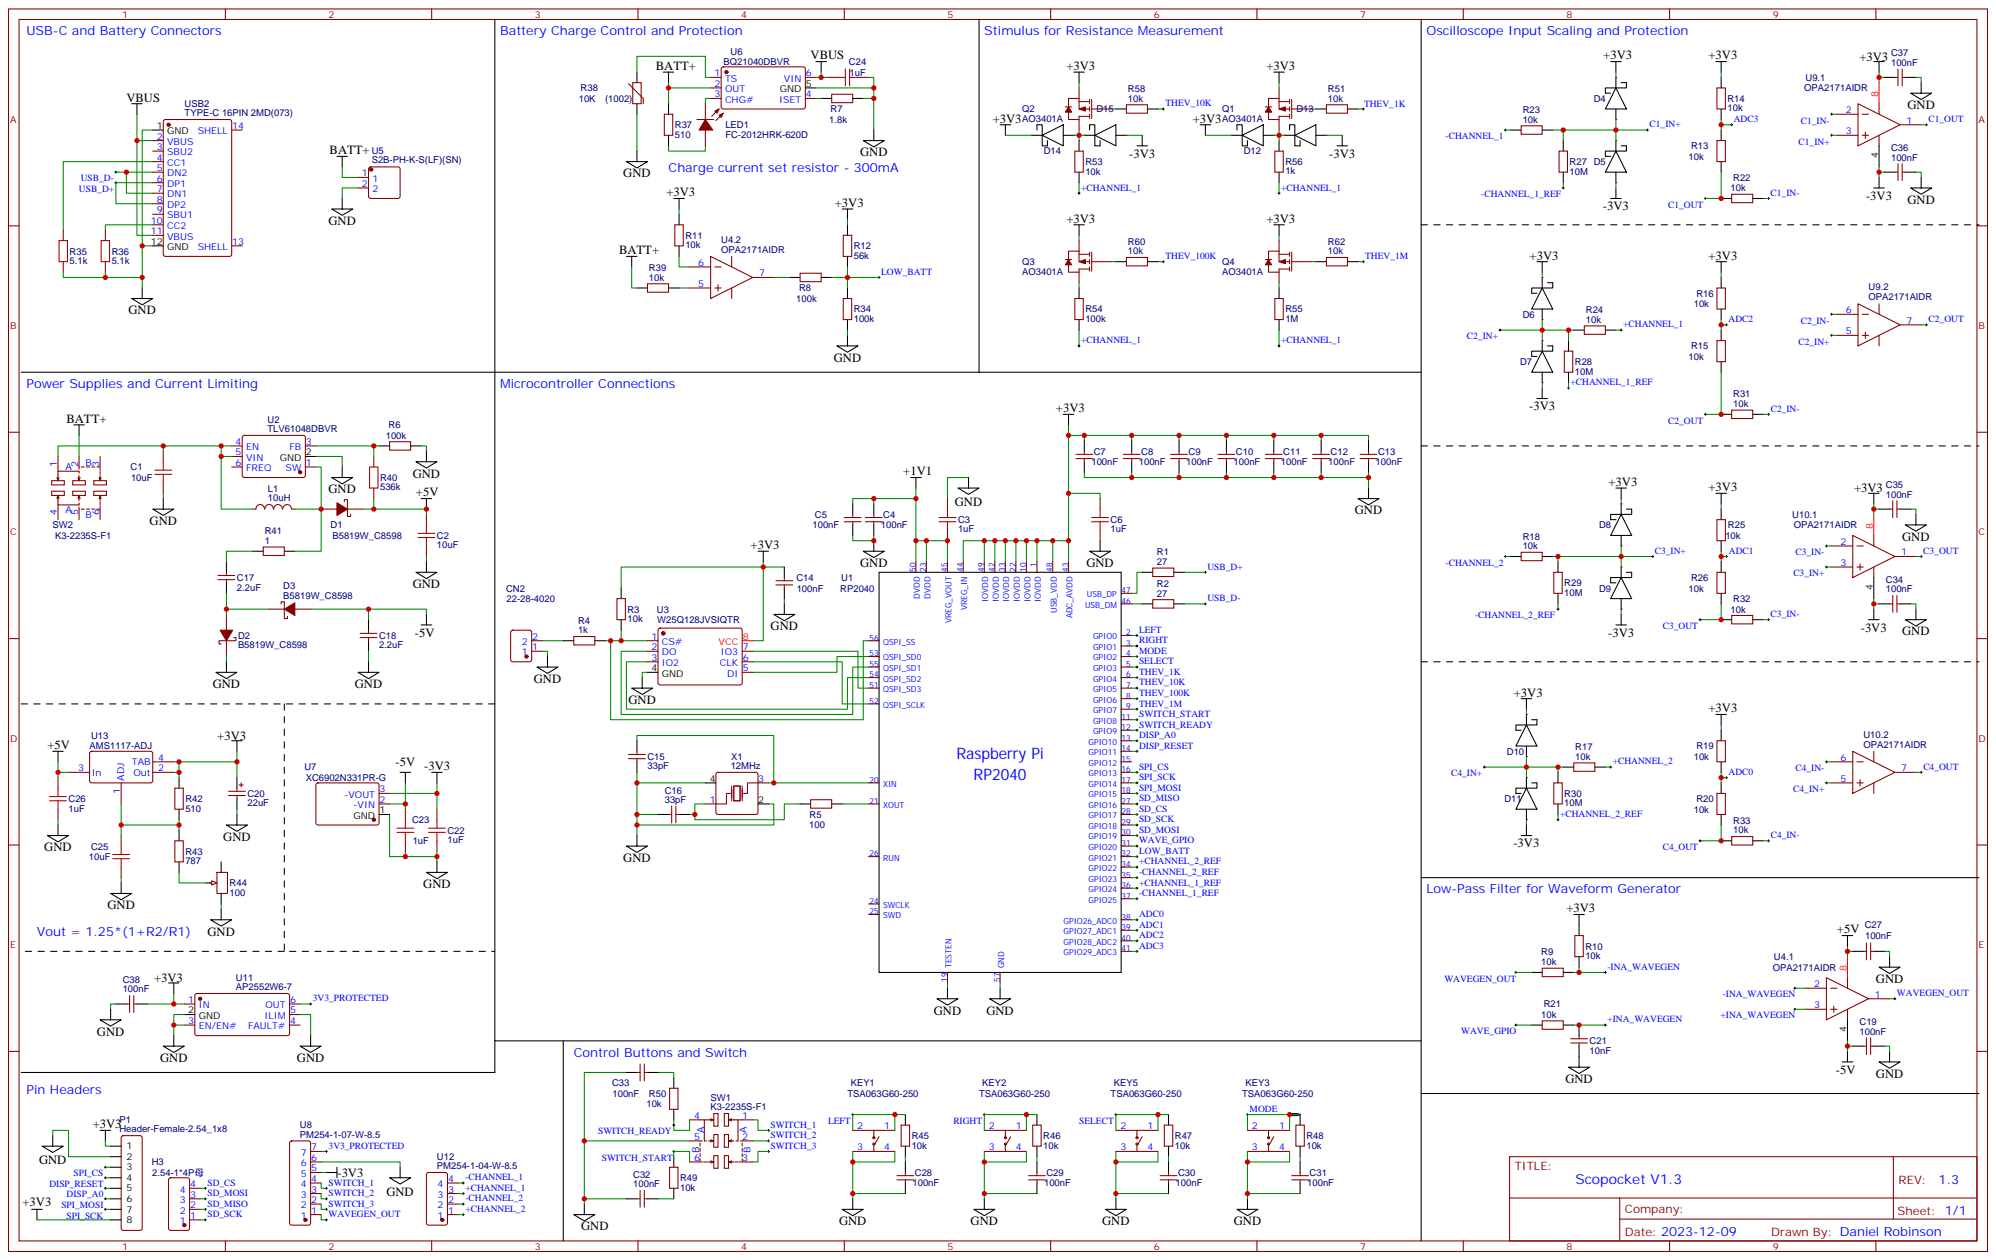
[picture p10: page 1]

Battery Charge Control and Protection

USB-C and Battery Connectors

Charge current set resistor - 300mA

Power Supplies and Current Limiting

Low-Pass Filter for Waveform Generator

Control Buttons and Switch

Drawn By: Daniel Robinson

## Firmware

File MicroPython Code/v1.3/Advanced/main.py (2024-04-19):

from machine import Timer, Pin, PWM, ADC, SPI, mem32, freq
import _thread
import time
import data
from ST7735 import TFT
from sysfont import sysfont
import adc_functions

def startDAC():
    global core1
    waveformSetting = settings[4][1][settings[4][0]]
    waveformFreq = settings[5][1][settings[5][0]]
    waveformAmp = settings[6][1][settings[6][0]]
    
    if(waveformFreq == "1Hz"):
        period = 1000000
    elif(waveformFreq == "5Hz"):
        period = 200000
    elif(waveformFreq == "10Hz"):
        period = 100000
    
    if(waveformAmp == "1V"):
        amplitude = 1
    elif(waveformAmp == "2V"):
        amplitude = 2
    elif(waveformAmp == "3V"):
        amplitude = 3
    elif(waveformAmp == "3.3V"):
        amplitude = 3.3
    
    if(waveformSetting == "sine"):
        core1 = _thread.start_new_thread(dac, (sine, period, amplitude))
    if(waveformSetting == "triangle"):
        core1 = _thread.start_new_thread(dac, (tri, period, amplitude))
    if(waveformSetting == "square"):
        core1 = _thread.start_new_thread(dac, ([32768, 65535], period, amplitude))

def dac(waveform, period_us, amplitude):
    global waveDAC, dac_active
    
    num_samples = len(waveform)
    time_step = int(period_us / num_samples)
    
    scaled_waveform = [0]*num_samples
    for x in range(num_samples):
        scaled_waveform[x] = int((waveform[x] - 32768) * amplitude / 3.3 + 32768)
    
    dac_step = 0
    current_time = time.ticks_us()
    while dac_active:
        initial_time = current_time
        waveDAC.duty_u16(int(scaled_waveform[dac_step]))
        dac_step += 1
        if(dac_step == num_samples):
            dac_step = 0
        while(True):
            current_time = time.ticks_us()
            if time.ticks_diff(current_time, initial_time) >= time_step - 1:
                break
    return
        
'''
def startDAC():
    global dacTimer
    waveformSetting = settings[4][1][settings[4][0]]
    if(waveformSetting == "sine"):
        dacTimer = Timer(mode=Timer.PERIODIC, period=1, callback=sineDacHandler)
    if(waveformSetting == "triangle"):
        dacTimer = Timer(mode=Timer.PERIODIC, period=1, callback=triDacHandler)
    if(waveformSetting == "square"):
        dacTimer = Timer(mode=Timer.PERIODIC, period=1, callback=sqrDacHandler)
        
def stopDAC():
    global dacTimer
    dacTimer.deinit()

def sineDacHandler(timer):
    global dacStep, waveDAC
    waveDAC.duty_u16(int(sine[dacStep]))
    if (dacStep != 999):
        dacStep += 1
    else:
        dacStep = 0

def triDacHandler(timer):
    global dacStep, waveDAC
    waveDAC.duty_u16(int(tri[dacStep]))
    if (dacStep != 999):
        dacStep += 1
    else:
        dacStep = 0

def sqrDacHandler(timer):
    global dacStep, waveDAC
    if (dacStep < 500):
        waveDAC.duty_u16(65535)
    else:
        waveDAC.duty_u16(32768)
    if (dacStep != 999):
        dacStep += 1
    else:
        dacStep = 0
'''
def slowMeasure(sample_period_us):
    global C1, C1Ref, C2, C2Ref, ADCDataC1, ADCDataC2, voltageDataC1, voltageDataC2
    current_time = time.ticks_us()
    for x in range(160):
        initial_time = current_time
        ADCDataC1[x] = C1.read_u16() - C1Ref.read_u16()
        ADCDataC2[x] = C2.read_u16() - C2Ref.read_u16()
        while(True):
            current_time = time.ticks_us()
            if time.ticks_diff(current_time, initial_time) >= sample_period_us:
                break
    newVoltageFactor = voltageFactor/16
    for x in range(160):
        voltageDataC1[x] = newVoltageFactor*(ADCDataC1[x])
        voltageDataC2[x] = newVoltageFactor*(ADCDataC2[x])

def measure():
    global ADCDataC1, ADCDataC2, voltageDataC1, voltageDataC2
    h_scale = settings[1][1][settings[1][0]]
    measured_data = 0
    if h_scale == "100ms/div":
        slowMeasure(10000)
    if h_scale == "10ms/div":
        slowMeasure(1000)
    if h_scale == "1ms/div":
        measured_data = adc_functions.multiSample(4, 1200, 160)
    if h_scale == "100us/div":
        measured_data = adc_functions.multiSample(4, 120, 160)
    if h_scale == "1ms/div" or h_scale == "100us/div":
        for x in range(160):
            ADCDataC1[x] = measured_data[4*x] - measured_data[4*x + 1]
            ADCDataC2[x] = measured_data[4*x + 2] - measured_data[4*x + 3]
            voltageDataC1[x] = voltageFactor*(ADCDataC1[x])
            voltageDataC2[x] = voltageFactor*(ADCDataC2[x])

def plot():
    global yValsC1, yValsC2, ADCDataC1, ADCDataC2, tft, cursorPos
    for x in range(160):
        yValsC1[x] = int(69-displayFactor*voltageDataC1[x])
        yValsC2[x] = int(69-displayFactor*voltageDataC2[x])
        if(yValsC1[x] < 10):
            yValsC1[x] = 10
        if(yValsC2[x] < 10):
            yValsC2[x] = 10
        if(yValsC1[x] > 127):
            yValsC1[x] = 127
        if(yValsC2[x] > 127):
            yValsC2[x] = 127
        if(x > 0):
            tft.line((x-1, yValsC2[x-1]), (x, yValsC2[x]), TFT.BLUE)
            tft.line((x-1, yValsC1[x-1]), (x, yValsC1[x]), TFT.RED)
    cursorPos = 0

def updateText():
    global tft
    h_scale = settings[1][1][settings[1][0]]
    if h_scale == "100ms/div":
        tft.text((0, 0), '{:.2f}s'.format(cursorPos*0.01), TFT.GREEN, sysfont, 1, nowrap=True)
    elif h_scale == "10ms/div":
        tft.text((0, 0), str(cursorPos*1) + "ms  ", TFT.GREEN, sysfont, 1, nowrap=True)
    elif h_scale == "1ms/div":
        tft.text((0, 0), '{:.1f}ms'.format(cursorPos*0.1), TFT.GREEN, sysfont, 1, nowrap=True)
    elif h_scale == "100us/div":
        tft.text((0, 0), '{:.2f}ms'.format(cursorPos*0.01), TFT.GREEN, sysfont, 1, nowrap=True)
    
    tft.text((40, 0), '{:+.2f}V'.format(voltageDataC1[cursorPos]), TFT.RED, sysfont, 1, nowrap=True)
    tft.text((90, 0), '{:+.2f}V'.format(voltageDataC2[cursorPos]), TFT.BLUE, sysfont, 1, nowrap=True)
    waveformSetting = settings[4][1][settings[4][0]]
    if(waveformSetting == "sine"):
        tft.text((140, 0), 'SIN', TFT.YELLOW, sysfont, 1, nowrap=True)
    elif(waveformSetting == "triangle"):
        tft.text((140, 0), 'TRI', TFT.YELLOW, sysfont, 1, nowrap=True)
    elif(waveformSetting == "square"):
        tft.text((140, 0), 'SQR', TFT.YELLOW, sysfont, 1, nowrap=True)

def drawAxes():
    tft.text((6, 8), 'v', TFT.YELLOW, sysfont, 1, nowrap=True)
    tft.text((155, 58), 's', TFT.YELLOW, sysfont, 1, nowrap=True)
    
    tft.vline((0,10), 118, TFT.YELLOW)
    tft.line((0,10), (3, 13), TFT.YELLOW)
    tft.line((0,127), (3, 124), TFT.YELLOW)

    tft.pixel((1,61), TFT.YELLOW)
    tft.pixel((1,53), TFT.YELLOW)
    tft.pixel((1,45), TFT.YELLOW)
    tft.pixel((1,37), TFT.YELLOW)
    tft.pixel((1,29), TFT.YELLOW)
    tft.pixel((1,21), TFT.YELLOW)

    tft.pixel((1,77), TFT.YELLOW)
    tft.pixel((1,85), TFT.YELLOW)
    tft.pixel((1,93), TFT.YELLOW)
    tft.pixel((1,101), TFT.YELLOW)
    tft.pixel((1,109), TFT.YELLOW)
    tft.pixel((1,117), TFT.YELLOW)

    tft.hline((1,69), 159, TFT.YELLOW)
    tft.line((159, 69), (156, 72), TFT.YELLOW)
    tft.line((159, 69), (156, 66), TFT.YELLOW)

    for x in range(15):
        tft.pixel((10 + 10*x,68), TFT.YELLOW)
        tft.pixel((10 + 10*x,70), TFT.YELLOW)

def moveCursor(newPos):
    global cursorPos
    tft.vline((cursorPos, 10), 118, TFT.BLACK)
    drawAxes()
    if(newPos == cursorPos + 1): # moving right
        tft.line((cursorPos, yValsC2[cursorPos]), (newPos, yValsC2[newPos]), TFT.BLUE)
        tft.line((cursorPos, yValsC1[cursorPos]), (newPos, yValsC1[newPos]), TFT.RED)
        if(cursorPos > 0):
            tft.line((cursorPos - 1, yValsC2[cursorPos - 1]), (cursorPos, yValsC2[cursorPos]), TFT.BLUE)
            tft.line((cursorPos - 1, yValsC1[cursorPos - 1]), (cursorPos, yValsC1[cursorPos]), TFT.RED)
    elif(newPos == cursorPos - 1): # moving left
        tft.line((cursorPos, yValsC2[cursorPos]), (newPos, yValsC2[newPos]), TFT.BLUE)
        tft.line((cursorPos, yValsC1[cursorPos]), (newPos, yValsC1[newPos]), TFT.RED)
        if(cursorPos < 159):
            tft.line((cursorPos + 1, yValsC2[cursorPos + 1]), (cursorPos, yValsC2[cursorPos]), TFT.BLUE)
            tft.line((cursorPos + 1, yValsC1[cursorPos + 1]), (cursorPos, yValsC1[cursorPos]), TFT.RED)
    else: # jump
        tft.pixel((cursorPos, yValsC2[cursorPos]),TFT.BLUE)
        tft.pixel((cursorPos, yValsC1[cursorPos]),TFT.RED)
        
    cursorPos = newPos
    #tft.pixel((cursorPos, yValsC2[cursorPos]),TFT.BLUE)
    #tft.pixel((cursorPos, yValsC1[cur  sorPos]),TFT.RED)
    tft.vline((cursorPos, 10), 118, TFT.GREEN)

def openMenu():
    global tft, leftButton, rightButton, leftCounter, rightCounter, selectButton, selectCounter, modeButton, modeCounter, settings, cursorPos, dac_active
    dac_active = False
    tft.fill(TFT.BLACK)
    tft.text((0, 0 ), 'Vert.  Scale:', TFT.WHITE, sysfont, 1, nowrap=True)
    tft.text((0, 12), 'Horiz. Scale:', TFT.WHITE, sysfont, 1, nowrap=True)
    tft.text((0, 24), 'Trigger Type:', TFT.WHITE, sysfont, 1, nowrap=True)
    tft.text((0, 36), 'Trigg. level:', TFT.WHITE, sysfont, 1, nowrap=True)
    tft.text((0, 48), 'Function Out:', TFT.WHITE, sysfont, 1, nowrap=True)
    tft.text((0, 60), 'Function Frq:', TFT.WHITE, sysfont, 1, nowrap=True)
    tft.text((0, 72), 'Function Amp:', TFT.WHITE, sysfont, 1, nowrap=True)
    menuIndex = 0
    updateMenuSelection(menuIndex)
    while(True):
        time.sleep(0.001)
        if (not leftButton.value()):
            leftCounter += 1
            if (leftCounter == 5):
                settings[menuIndex][0] = settings[menuIndex][0] - 1
                if(settings[menuIndex][0] < 0):
                    settings[menuIndex][0] = len(settings[menuIndex][1]) - 1
                updateMenuSelection(menuIndex)
        else:
            leftCounter = 0
    
        if (not rightButton.value()):
            rightCounter += 1
            if (rightCounter == 5):
                settings[menuIndex][0] = settings[menuIndex][0] + 1
                if(settings[menuIndex][0] >= len(settings[menuIndex][1])):
                    settings[menuIndex][0] = 0
                updateMenuSelection(menuIndex)
        else:
            rightCounter = 0
        
        if (not modeButton.value()):
            modeCounter += 1
            if (modeCounter == 5):
                break
        else:
            modeCounter = 0
        
        if (not selectButton.value()):
            selectCounter += 1
            if (selectCounter == 5):
                menuIndex += 1
                if menuIndex == len(settings):
                    break
                updateMenuSelection(menuIndex)
        else:
            selectCounter = 0
    dac_active = True
    startDAC()
    tft.fill(TFT.BLACK)
    drawAxes()
    cursorPos = 0

def updateMenuSelection(menuIndex):
    global tft
    tft.fillrect((80,12*menuIndex - 4), (99, 14), TFT.BLACK)
    tft.hline((80, 12*menuIndex + 9), 6*len(settings[menuIndex][1][settings[menuIndex][0]]), TFT.RED)
    for x in range(len(settings)):
        if x == 3 and settings[2][1][settings[2][0]] == "Switch":
            tft.text((80, 36), "n/a", TFT.GRAY, sysfont, 1, nowrap=True)
        else:
            tft.text((80, x*12), settings[x][1][settings[x][0]] + "      ", TFT.GREEN, sysfont, 1, nowrap=True)

spi = SPI(1, baudrate=133000000, polarity=0, phase=0, sck=Pin(14), mosi=Pin(15), miso=Pin(12))
tft=TFT(spi,10,11,13)
tft.initr()
tft.rgb(True)
tft.rotation(3)
tft.fill(TFT.BLACK)
drawAxes()

sine = data.sineWave()
tri = data.triWave()
wavePin = Pin(20, mode=Pin.OUT)
waveDAC = PWM(wavePin)
waveDAC.freq(1000000)
dacStep = 0

C1Ref = ADC(29)
C1 = ADC(28)
C2Ref = ADC(27)
C2 = ADC(26)

c1gnd = Pin(25, Pin.OUT)
c1gnd.value(0)
c2gnd = Pin(24, Pin.OUT)
c2gnd.value(0)
c3gnd = Pin(23, Pin.OUT)
c3gnd.value(0)
c4gnd = Pin(22, Pin.OUT)
c4gnd.value(0)

thev1k = Pin(4, Pin.OUT)
thev1k.value(1)
thev10k = Pin(5, Pin.OUT)
thev10k.value(1)
thev100k = Pin(6, Pin.OUT)
thev100k.value(1)
thev1M = Pin(7, Pin.OUT)
thev1M.value(1)

voltageFactor = 6.7/4096
displayFactor = 16
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

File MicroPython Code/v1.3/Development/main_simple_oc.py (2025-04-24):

from machine import Timer, Pin, PWM, ADC, SPI, mem32
from array import array
from uctypes import addressof
import time
import data
from ST7735 import TFT
from sysfont import sysfont

machine.freq(192_000_000)

# define DMA register addresses
DMA_BASE = 0x50000000

CH2_READ_ADDR   = DMA_BASE+0x080
CH2_WRITE_ADDR  = DMA_BASE+0x084
CH2_TRANS_COUNT = DMA_BASE+0x088
CH2_CTRL_TRIG   = DMA_BASE+0x08c

CH3_READ_ADDR   = DMA_BASE+0x0c0
CH3_WRITE_ADDR  = DMA_BASE+0x0c4
CH3_TRANS_COUNT = DMA_BASE+0x0c8
CH3_CTRL_TRIG   = DMA_BASE+0x0cc

DMA_TIMER0 = DMA_BASE + 0x420

# define PWM register addresses

PWM_BASE = 0x40050000

CH2_DIV = PWM_BASE + 0x2c
CH2_CC = PWM_BASE + 0x34
CH2_TOP = PWM_BASE + 0x38

def startTimers():
    global measurementTimer, plottingTimer
    #dacTimer = Timer(mode=Timer.PERIODIC, period=1, callback=dacHandler)
    measurementTimer = Timer(mode=Timer.PERIODIC, period=10, callback=measurementHandler)
    plottingTimer = Timer(mode=Timer.PERIODIC, period=10, callback=plottingHandler)

def stopTimers():
    global measurementTimer, plottingTimer
    #dacTimer.deinit()
    measurementTimer.deinit()
    plottingTimer.deinit()

def convertRawToVoltage(u16_val):
    return (u16_val - cal_0_value) * voltageFactor
'''
def dacHandler(timer):
    global dacStep, waveDAC
    if(mode[modeIndex] == "SIN" or mode[modeIndex] == "PWR" or mode[modeIndex] == "PHS"):
        waveDAC.duty_u16(int(sine[dacStep]))
    elif(mode[modeIndex] == "SQR"):
        if (dacStep < 500):
            waveDAC.duty_u16(65535)
        else:
            waveDAC.duty_u16(32768)
    if (dacStep != 999):
        dacStep += 1
    else:
        dacStep = 0
'''
#2-channel chained DMA for DAC output. channel 2 does the transfer, channel 3 reconfigures
p=array('I',[0]) #global 1-element array
def dac_dma(ar,nword):
    #first disable the DMAs to prevent corruption while writing
    mem32[CH2_CTRL_TRIG]=0
    mem32[CH3_CTRL_TRIG]=0
    #setup first DMA which does the actual transfer
    mem32[CH2_READ_ADDR]=addressof(ar)
    mem32[CH2_WRITE_ADDR]=CH2_CC
    mem32[CH2_TRANS_COUNT]=nword
    mem32[DMA_TIMER0] = 0x0001FA00 # divide system clock by 64000 = 3000 samples per second
    IRQ_QUIET=0x1 #do not generate an interrupt
    TREQ_SEL=0x3b #timer 0 triggered
    CHAIN_TO=3    #start channel 3 when done
    RING_SEL=0
    RING_SIZE=0   #no wrapping
    INCR_WRITE=0  #for write to array
    INCR_READ=1   #for read from array
    DATA_SIZE=2   #32-bit word transfer
    HIGH_PRIORITY=1
    EN=1
    CTRL2=(IRQ_QUIET<<21)|(TREQ_SEL<<15)|(CHAIN_TO<<11)|(RING_SEL<<10)|(RING_SIZE<<9)|(INCR_WRITE<<5)|(INCR_READ<<4)|(DATA_SIZE<<2)|(HIGH_PRIORITY<<1)|(EN<<0)
    mem32[CH2_CTRL_TRIG]=CTRL2
    #setup second DMA which reconfigures the first channel
    p[0]=addressof(ar)
    mem32[CH3_READ_ADDR]=addressof(p)
    mem32[CH3_WRITE_ADDR]=CH2_READ_ADDR
    mem32[CH3_TRANS_COUNT]=1
    IRQ_QUIET=0x1 #do not generate an interrupt
    TREQ_SEL=0x3f #no pacing
    CHAIN_TO=2    #start channel 2 when done
    RING_SEL=0
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

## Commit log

2023-06-07 Uploaded design files
    [BOM_PCB_WavegenOscilloscopeSwitch copy_2023-06-06.csv, PickAndPlace_PCB_WavegenOscilloscopeSwitch copy_2023-06-06.csv]
2023-07-25 Reorganized files
    [BOM_PCB_WavegenOscilloscopeSwitch copy_2023-06-06.csv, PickAndPlace_PCB_WavegenOscilloscopeSwitch copy_2023-06-06.csv]
2023-09-04 Added settings menu allowing changing waveform, enabling power plot mode, and trigger
2023-09-05 Adjusted scale of power plot mode
2023-11-22 Updated power plot mode to trigger on channel 1 peak
2024-04-16 Added version 1.3 PCB design files and case
    [BOM_PCB_WavegenOscilloscopeSwitch copy_2023-06-06.csv, BOM_ScopocketV1.3_2024-04-16.csv, PickAndPlace_PCB_ScopocketV1.3_2024-04-16.csv, PickAndPlace_PCB_Wavege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]
2024-04-17 Fixed pin reference page
2024-08-12 Added case with pin label slot and added pin label gerber file
    [scopocket_case_left.STL, scopocket_case_right.STL]
2025-04-24 Updated simple firmware to improve resistance measurement, waveform generation, and voltage measurement accuracy
2025-04-27 Fixed power mode display bugs
2025-05-26 Added 4-channel calibration, added Canvas link to scopocket.com
